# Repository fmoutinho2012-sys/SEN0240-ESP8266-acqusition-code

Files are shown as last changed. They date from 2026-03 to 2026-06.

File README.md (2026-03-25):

#### This repository provides the software stack for a high-fidelity surface electromyography (sEMG) acquisition system designed for benchmarking low-cost hardware against clinical-grade standards. 
#### The system utilizes an ESP8266 microcontroller and an ADS1015 12-bit ADC (connected to SEN0240 sEMG vía I2C)  to achieve a deterministic sampling rate of 1000 SPS, ensuring strict temporal and spectral alignment with reference databases such as NinaPro DB1.
The firmware is implemented in MicroPython and utilizes an optimized binary data-streaming protocol. This method ensures a stable 1000 Hz sampling frequency by bypassing the Flash memory write latency of the ESP8266. The accompanying offline Python engine performs the complete digital signal processing pipeline, including 4th-order Butterworth band-pass filtering (20–450 Hz), 50 Hz digital notch filtering, full-wave rectification, linear envelope extraction via a 3 Hz leaky integrator, and polyphase resampling to 100 Hz.
#### Hardware integration requires an ESP8266 clocked at 160 MHz connected to an ADS1015 via I2C on GPIO 0 (SCL) and GPIO 2 (SDA). The ADC address must be set to 0x48 by grounding the ADDR pin. The DFRobot SEN0240 sensor is connected to channels A0 and A1 in differential mode.
#### Experimental validation across multiple subjects demonstrated an average Signal-to-Noise Ratio (SNR) over 29 dB and Pearson correlation of 0.80 morphological correlation with clinical-grade signals. This project proves that clinical-level sEMG acquisition requirements can be met using accessible off-the-shelf components.

### Repository Structure:
### -Firmware: MicroPython code for the ESP8266 (acquisition program):
* $${\color{LightBlue} \text{EMG\\_ADS1015\\_1000SPS\\_80s\\_v4.py}}$$   -High-speed binary acquisition script via i2c with ADS1015
### -Processing: Python scripts for PC-based data analysis (to obtain statistics peak, MAV, RMS, WL and visualization):
* $${\color{LightBlue} \text{plotter\\_data(10Rx8seg)\\_binary\\_mv\\_stats\\_2.py}}$$
### -Pearson Correlation Analysis:
* ### -Pearson Correlation Analysis:
* $${\color{LightBlue} \text{Pearson\\_correlation\\_validator\\_with\\_OFFSET\\_SAMPLES.py}}$$
### -Classification: Implements a Random Forest Classifier
* $${\color{LightBlue} \text{sEMG\\_Gesture\\_Recognition.py}}$$
### -SNR Analysis:
* $${\color{LightBlue} \text{sEMG\\_SNR\\_calculator.py}}$$

## Installation & Usage:
Install MicroPython on your ESP8266. Note: This project was developed using an ESP8266 with 1MB of Flash memory.
1. **Prepare the Hardware:** Install **MicroPython** on your ESP8266.
2. **Upload the Firmware:** Transfer `EMG_ADS1015_1000SPS_80s_v4.py` to the board using **Thonny** or your preferred IDE.
3. **Data Acquisition:** Run the script to start the recording.
   * *Note: The protocol lasts 80 seconds, consisting of 10 repetitions (5s active / 3s rest).*
4. **Data Transfer:** Once finished, download the generated `.bin` file to your PC for processing.

## Offline DSP Processing (PC)
### Offline DSP Processing (PC)
Ensure you have **Python** installed with the following libraries:
* `numpy`
* `matplotlib`
* `scipy`
#### Process and visualize the data (binary):

* * **Run:** `python plotter_data(10Rx8seg)_binary_mv_stats_2.py` &nbsp; `gesture_file.bin`

* This software processes the acquired binary data by applying a **DSP pipeline** to extract key EMG features.
* The results—including **Peak, MAV, RMS, and Waveform Length (WL)**—are calculated and reported via the console.
* Finally, the script generates a **visual plot** of the processed signal for analysis.

## DSP Pipeline Details
To match clinical standards, the raw signal undergoes the following stages:
* DC Offset Removal: Centering the signal at 0 mV.
* Band-pass Filter: 4th-order Butterworth (20–450 Hz).
* Notch Filter: Digital IIR at 50 Hz (Q =30).
* Full-wave Rectification: Extracting signal magnitude.
* Linear Envelope: 3 Hz low-pass filter (Leaky Integrator).
* Downsampling: Polyphase resampling to 100 Hz for NinaPro alignment.

### Pearson correlation analysis
#### Configuration
Before running the script, ensure you edit the following fields with the appropriate values inside the code:
* `user_file= = 'fist_gesture_raw_2.bin'`
* `FILE_MAT_NINAPRO = 'S1_A1_E2.mat'`
* `GESTURE_ID = 6`
* `CHANNELS_NINA = 2`
* `OFFSET_SAMPLES = 105`
* **Run:** &nbsp; `python  Pearson_correlation_validator_with_OFFSET_SAMPLES.py`

* This script is designed to estimate the Pearson correlation coefficient for each gesture. 
* The software compares the input binary data directly against the NinaPro DB1 database.
* Requirements:
* The script must be located in the same folder as the binary data file.
* The NinaPro database file (S1_A1_E2) must also be present in the same directory.
* Output:
Visualization: A plot comparing the acquired binary signal vs. the NinaPro reference.(correlation factor included in the plot).
Console Report: Prints the final calculated Pearson correlation factor.

### Classification: Implements a Random Forest Classifier with 5-fold Stratified Cross-Validation to benchmark system accuracy for both 3-gesture sets and binary command sets.
### Requirements
To run the analysis, you need Python 3.8+ and the following libraries:
* numpy: For numerical processing and vector operations.
* scipy: For signal processing (filters and resampling).
* scikit-learn: For the Random Forest model and statistical validation metrics.
* matplotlib: (Optional) For signal visualization.

 ##Install dependencies via pip:
code
Bash
* pip install numpy scipy scikit-learn

## How to Use
Place your all .bin files in the same directory as the script.
Ensure filenames contain the gesture labels: fist, thumb, or spread.
### Execute the script:
code
Bash
* **Run:** &nbsp; `python sEMG_Gesture_Recognition.py`
 
* This software implements a Random Forest classifier using 1,440 sliding windows (200 ms width, 50% overlap).
* It evaluates performance across three distinct gestures and generates a detailed confusion matrix.
* Outputs:
* Confusion matrix for analysis (table 3)
* Step-by-step processing logs (Feature extraction to benchmarking).

### SNR analysis:
* **Run:** &nbsp; `python sEMG_SNR_calculator.py gesture_file.bin`

* The program will detect the noise floor and the peak value in the current session
* The results will be reported by console and also a visulazation of the curve.
### Noise Window Adjustment (Offset)

The script uses a specific **rest window** to measure the hardware base noise (electronic interference) before the muscle is activated.

#### **What is it for?**
This window (set by default from samples **2000 to 3000**) is taken during the rest period (`DUR_REST`). The script calculates the average of this signal to "clean" the background noise and obtain an accurate **SNR (Signal-to-Noise Ratio)**. If your rest signal starts earlier or later, you must move this window to avoid accidentally capturing the beginning of the muscle contraction.

#### **How to change the values?**
Look for the following line inside the `perform_ensemble_analysis` function:

* pythoncode:
## Rest window: from 200 to 300 (100Hz scale = 2000 to 3000 original)
seg_raw_rest = raw_100[start + 200 : start + 300]
* First value (200): The starting point of the noise sample.
* Second value (300): The ending point of the noise sample.
### [!IMPORTANT]
* Scale Note: Since the code processes data resampled at 100Hz, you must divide the original sample value by 10.
* Example: To analyze from sample 1500 to 2500, you should enter [start + 150 : start + 250].
#### **Example Output (Console Report)**
When the script finishes, it will display a technical characterization in the console:

### SNR Report example:
* ======================================================================
 * TECHNICAL CHARACTERIZATION: fist_gesture_raw_2.bin
* ======================================================================
 1. Processed Signal Peak (Asignal):           8.57 mV
 2. Raw Input Noise (Offset 2k-3k):            3.79 mV
 3. Residual Noise (Post-DSP RMS):            0.3119 mV
* ---------------------------------------------------------------------
 * Filtering Efficiency:                         94.18 %
 * Signal-to-Noise Ratio (SNR dB):               28.78 dB
* ======================================================================

### Contac: 
* Author: Fernando Moutinho
* Contact: fmoutinho2012@gamil.com

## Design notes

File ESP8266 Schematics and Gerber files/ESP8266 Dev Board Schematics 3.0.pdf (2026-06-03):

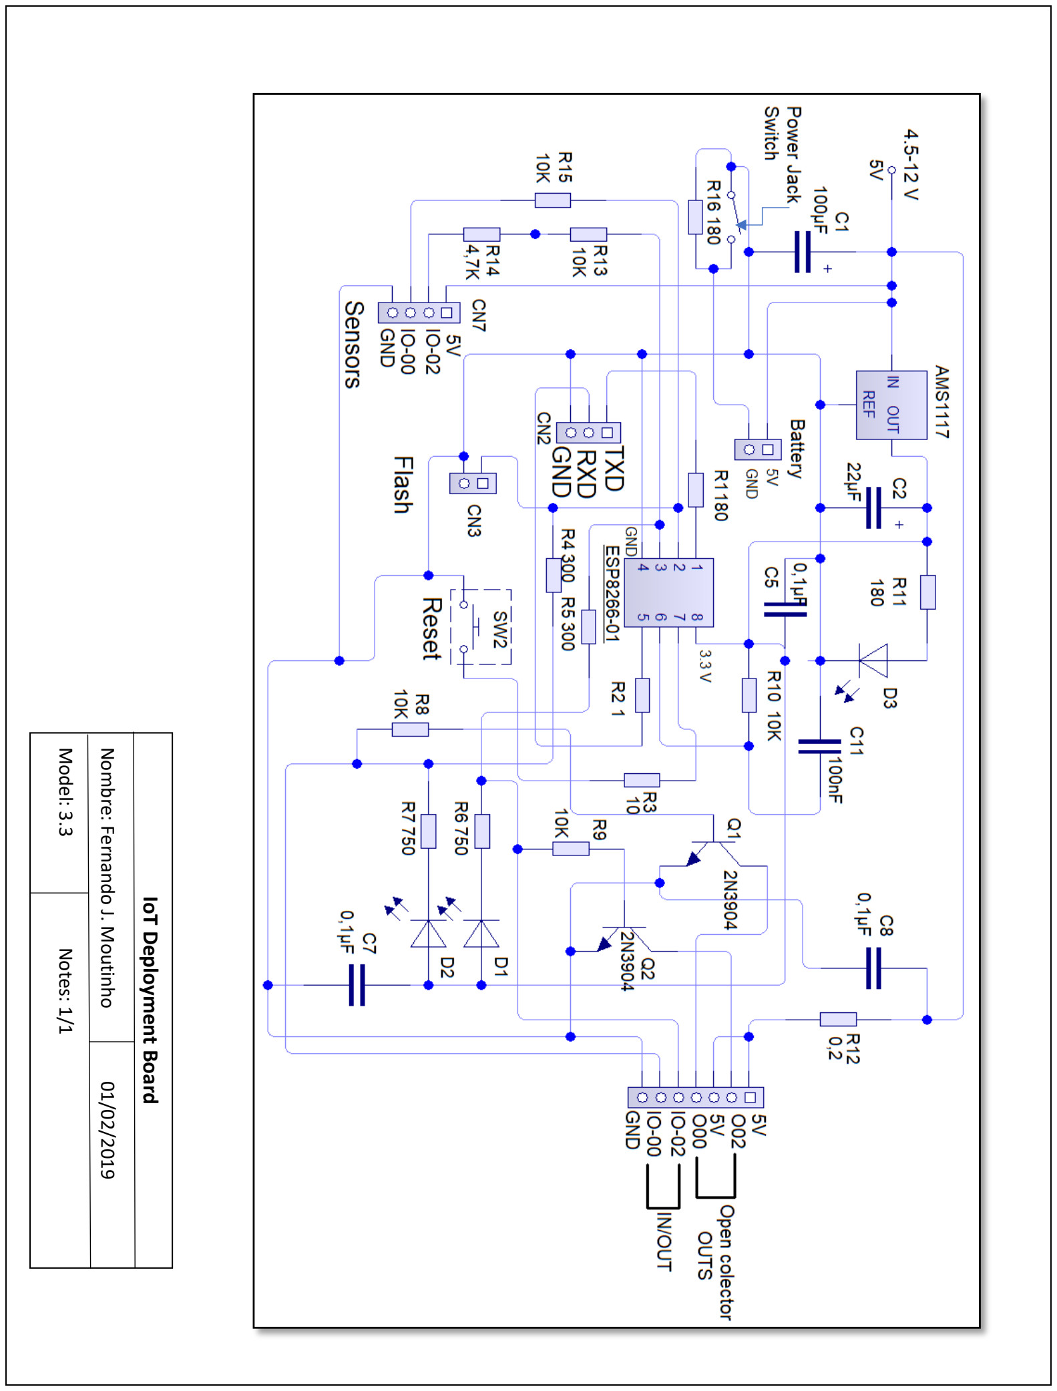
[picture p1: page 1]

IoT Deployment Board

Nombre: Fernando J. Moutinho 01/02/2019

Model: 3.3 Notes: 1/1

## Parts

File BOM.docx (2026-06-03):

Bill of Materials (BOM)

Designator | Component | Number | Cost per unit (€) | Total cost (€) | Source of materials
U1 | SEN0240 sEMG Induction Sensor | 1 | 42.50 | 42.50 | DFRobot (https://www.dfrobot.com) or local distributor
U2 | ESP8266 NodeMCU V3 Microcontroller | 1 | 4.50 | 4.50 | Generic electronics store / Amazon
U3 | ADS1015 12-bit ADC Module | 1 | 2.50 | 2.50 | Generic electronics store / AliExpress
C1 | Jumper Wires / Breadboard connectors | 1 set | 0.00* | 0.00 | Existing laboratory stock
TOTAL | | | Subtotal: | 49.50

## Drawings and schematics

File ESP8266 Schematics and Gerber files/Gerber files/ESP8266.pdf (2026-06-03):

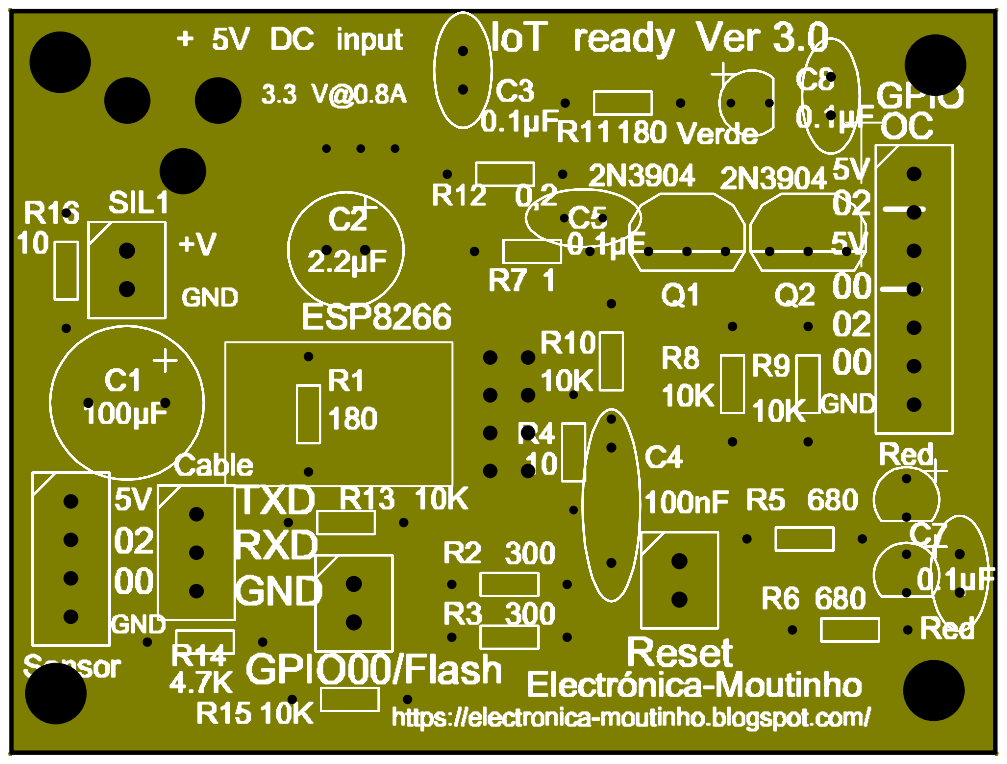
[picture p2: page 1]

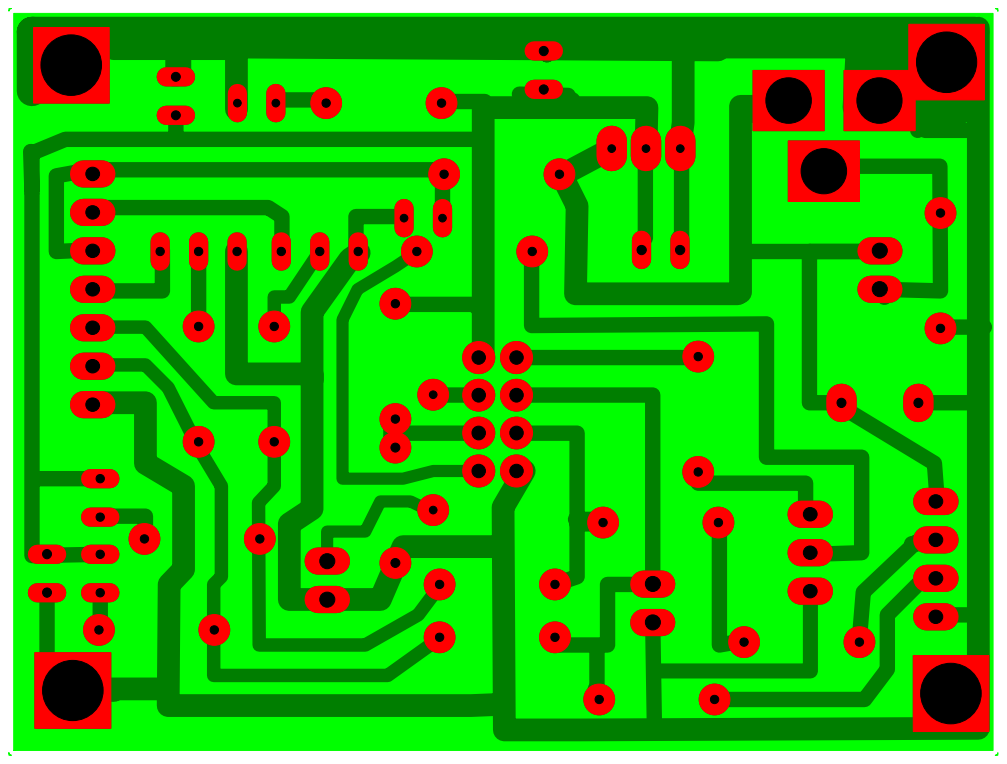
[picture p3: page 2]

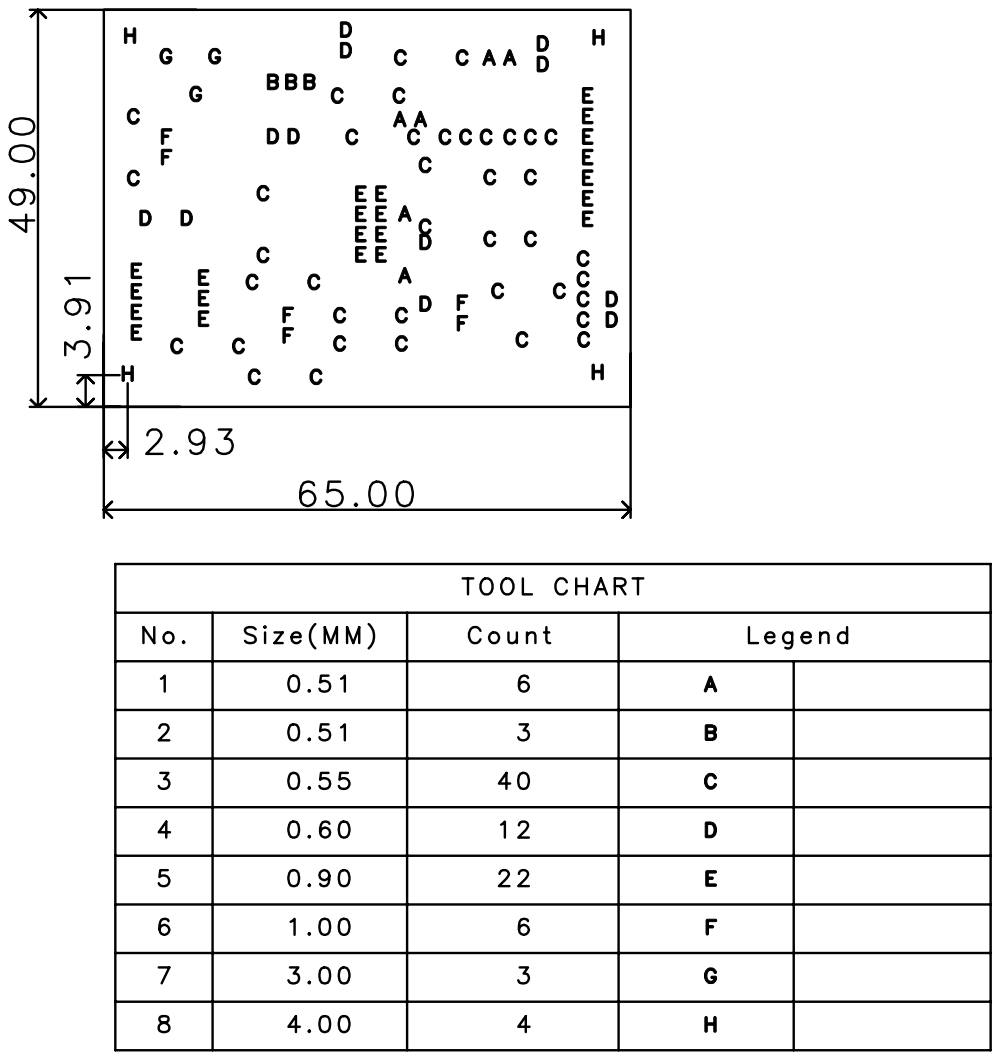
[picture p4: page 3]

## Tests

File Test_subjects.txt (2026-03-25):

Subjet Nº 1

Subject	Hand	Handedness	Gender	Age	Heigh	Weight	File
1	Intact	Right		Male	21	169	77	s1
2	Intact	Right		Female	32	172	57	s2
3	Intact	Right		Female	25	169	48	s3
4	Intact	Right		Male	39	171	83	s4
5	Intact	Right		Male	55	170	79	s5
6	Intact	Right		Male	41	171	73	s6

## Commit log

2026-03-16 Add files via upload
    File to be loaded onto the board (ESP8266 with MicroPython or ESP32): EMG_ADS1015_1000SPS_80s_V4.py (Data is saved in binary format, approx. 150kB).
    To process the binary data, use the Python script: plotter_data(10Rx8seg)_binary_mv.py.
2026-03-18 Add files via upload
    ### This repository contains the core processing and classification engine used in the study: "Reliability and Accuracy of a Low-Cost sEMG Acquisition System for Gesture Recognition: A Benchmarking S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
    ### Description:
    This Python script provides a complete end-to-end pipeline for processing surface Electromyography (sEMG) data captured with the DFRobot SEN0240 sensor and digitized via an ADS1015 (12-bit ADC) using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
    The script performs the following scientific tasks:
    **Binary Data Loading: Parses 16-bit binary files captured in real-time.
    * Digital Signal Processing (DSP):
    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
2026-03-25 Update EMG_ADS1015_1000SPS_80s_v4.py
    Acquisition Software (v4)
    This script is designed to be loaded onto the ESP8266 for EMG signal acquisition using the SEN0240 sensor.
    Sampling Rate: 1000 SPS
    Total Duration: 80 seconds
    Protocol: 10 repetitions of 8 seconds each (3s rest / 5s gesture activation).
2026-03-25 Acquisition software for ESP8266
    This script is designed to be loaded onto the ESP8266 for EMG signal acquisition using the SEN0240 sensor and ADS1015 ADC.Sampling Rate: 1000 SPS
    Data will be acquired in binary format: gesture.bin
    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
2026-03-25 DSP Pipeline & Statistical Analysis
    This software processes the acquired binary data by applying a DSP pipeline to extract key EMG features. The results, including Peak, MAV, RMS, and Waveform Length (WL), are calculated and reported v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
    Key Metrics:
    Signal Peak (Max): Maximum value in mV.
    MAV (Mean Absolute Value): Average of the absolute signal amplitude.
    RMS (Root Mean Square): Represents the power of the signal.
    Waveform Length (WL): Measure of signal complexity.
    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
2026-03-25 Pearson Correlation Analysis
    This script computes the Pearson correlation coefficient for each gesture by comparing input binary data directly against the NinaPro DB1 database.
    Requirements:
    The script must be located in the same directory as the binary data file.
    The NinaPro database file (S1_A1_E2) must be present in the same folder.
    Outputs:
    Visualization: A comparative plot of the acquired signal vs. the NinaPro reference (correlation factor included in the plot).
    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
2026-03-25 Gesture Recognition Model (Random Forest)
    This software implements a Random Forest classifier using 1,440 sliding windows (200 ms width, 50% overlap). It evaluates performance across three distinct gestures and generates a detailed confusion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
    Performance Summary:
    Dataset Audit: 1,440 feature vectors successfully extracted (Classes: [0, 1, 2]).
    Overall Accuracy (3-Gesture Set): 81.53%
    Binary Accuracy (Fist vs. Thumb): 89.69%
    Per-Gesture Recall:
    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
2026-03-25 SNR analysis.
    The script utilizes a specific rest window to measure hardware baseline noise (electronic interference) before muscle activation.
    What is it for?
    This window (default: samples 2000 to 3000) is captured during the rest period (DUR_REST). The script calculates the average of this signal to "clean" background noise and obtain an accurate SNR.
    Default window: 2k-3k samples.
